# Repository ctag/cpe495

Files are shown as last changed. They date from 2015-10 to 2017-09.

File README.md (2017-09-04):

# cpe495

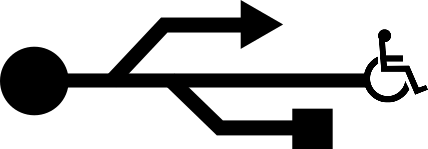
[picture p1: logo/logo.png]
Project Logo


UAH CPE495 "Adaptive H.I.D." senior design team.

## Current Development

Development on the 3.5mm adaptve button continues at https://github.com/ctag/clunke

## Git Formatting

* All paths and filenames should be camelCase.
* No binary files, they don't play well with git.
    * Images are an exception.

## Git Structure

* Git project for code, text documents.
* Github Wiki for research.
* Google Drive for presentations and binary files.

## What we're doing

Our team is researching and building Adaptive Technology interface devices to help people living with disabilities interact with computers.

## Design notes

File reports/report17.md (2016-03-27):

## Progress Report 17

Class | Week
----- | ----
CPE 496 | 9 Mar. 2016 -- 15 Mar. 2016

### Adaptive H.I.D.

<!--- This is a comment
Make sure to use *asterisks* to create italics on the member of whoever created the report
-->

* *Christopher Bero*
* Bryant Johnson
* John Gould
* Michael Baldwin

### Project Status
<!---
Project Status is a review of what was accomplished last week and a description of where we stand going into this sprint. A comparison between goals and actual accomplishments is a good idea.
-->

We are working to use the feedback provided at our last customer meeting to deliver another iteration of our prototype keyboard, along with an AT button to use with standardized 3.5mm cables found in many adaptive toys and machines.

### Difficulties Encountered

<!---
Difficulties Encountered is required. Other teams report losing points if this is missing.
Put here any trouble we had while accomplishing work during the previous sprint/week.
-->

Our 3D printer has developed a problem where the filament we have will swell slightly in some areas and bind inside of the hotend's mount. This causes us to lose the active print, as plastic stops extruding, and to recover we have to tear down the printer's extruder and remove the stuck filament.

### Next Sprint

<!---
Next Sprint should be a list of tasks that each member is going to work towards for the upcomming week.
Make sure to email members on Thursday or Friday so that they can respond with their most recent progress.
-->

* Christopher Bero:
    * Move 3d printer to makers local again
    * print button test base
* Michael Baldwin:
    * Continue work on predictive text application.
* John Gould:
    * Mediate testing and integration for hardware and software testing.
* Bryant Johnson:
    * Polyfill between hardware and software as support.

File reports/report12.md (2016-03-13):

## Progress Report 12

Class | Week
----- | ----
CPE 496 | 3 Feb. 2016 -- 9 Feb. 2016

### Adaptive H.I.D.

<!--- This is a comment
Make sure to use *asterisks* to create italics on the member of whoever created the report
-->

* *Christopher Bero*
* Bryant Johnson
* John Gould
* Michael Baldwin

### Project Status
<!---
Project Status is a review of what was accomplished last week and a description of where we stand going into this sprint. A comparison between goals and actual accomplishments is a good idea.
-->

We have finished development plans for our second keyboard prototype. It is currently being constructed.

Work on our desktop application is ongoing.

### Difficulties Encountered

<!---
Difficulties Encountered is required. Other teams report losing points if this is missing.
Put here any trouble we had while accomplishing work during the previous sprint/week.
-->

We upgraded from a 30W to 100W chemical laser bed and have had huge difficulties working with the control software. DXF if the preferred format for migrating an SVG model to the laser, but DXF files exported by Inkscape fail to be processed. We're working on an export format such as PLT or HPGL, but both crash a python script in Inkscape when invoked.

*Update Feb. 9*

We're closing in on a working method for designing and cutting files with the 100W laser bed. SVG files are exported as EPS, which is run through a script based on the `pstoedit` command line utility. This results in a useable DXF file which the laser computer recognizes. We're still investigating this approach, but it appears that color masks and layering works correctly.

### Next Sprint

<!---
Next Sprint should be a list of tasks that each member is going to work towards for the upcomming week.
Make sure to email members on Thursday or Friday so that they can respond with their most recent progress.
-->

* Christopher Bero:
    * Work on laser and keyboard hardware.
* Michael Baldwin:
    * Continue work on predictive text application.
* John Gould:
    * Mediate testing and integration for hardware and software testing.
* Bryant Johnson:
    * Polyfill between hardware and software as support.

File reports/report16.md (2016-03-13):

## Progress Report 16

Class | Week
----- | ----
CPE 496 | 2 Mar. 2016 -- 8 Mar. 2016

### Adaptive H.I.D.

<!--- This is a comment
Make sure to use *asterisks* to create italics on the member of whoever created the report
-->

* *Christopher Bero*
* Bryant Johnson
* John Gould
* Michael Baldwin

### Project Status
<!---
Project Status is a review of what was accomplished last week and a description of where we stand going into this sprint. A comparison between goals and actual accomplishments is a good idea.
-->

During this sprint we will meet with our customer again and go over the next keyboard prototype.
We went over various hardware design iterations. This sprint we tested the various methods of paddle actuation stiffness for the keyboard.

### Difficulties Encountered

<!---
Difficulties Encountered is required. Other teams report losing points if this is missing.
Put here any trouble we had while accomplishing work during the previous sprint/week.
-->

Different tension springs were causing problems. Need to purchase 3mm couplers for the keyboards layers.
Might need to buy spacers if not available. We were able to create a more streamlined solution for our laser cutter. Prototypes are being created at a much faster pace. 

### Next Sprint

<!---
Next Sprint should be a list of tasks that each member is going to work towards for the upcomming week.
Make sure to email members on Thursday or Friday so that they can respond with their most recent progress.
-->

* Christopher Bero:
    * Build second prototype keyboard.
* Michael Baldwin:
    * Continue work on predictive text application.
* John Gould:
    * Mediate testing and integration for hardware and software testing.
* Bryant Johnson:
    * Polyfill between hardware and software as support.

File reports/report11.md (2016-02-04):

## Progress Report 11

Class | Week
----- | ----
CPE 496 | 27 Jan. 2016 -- 2 Feb. 2016

### Adaptive H.I.D.

<!--- This is a comment
Make sure to use *asterisks* to create italics on the member of whoever created the report
-->

* Christopher Bero
* *Bryant Johnson*
* John Gould
* Michael Baldwin

### Project Status
<!---
Project Status is a review of what was accomplished last week and a description of where we stand going into this sprint. A comparison between goals and actual accomplishments is a good idea.
-->

We are working on our topical presentation, we will discuss the prospective future of consumer 3d printing with the class as well as the tests and findings we obtained through operation of our own printer.

Current goal is to design and upload a website detailing our project's goals and progress. 

We outlined our individual short term goals for this semester. 

### Difficulties Encountered

<!---
Difficulties Encountered is required. Other teams report losing points if this is missing.
Put here any trouble we had while accomplishing work during the previous sprint/week.
-->

Continual time conflicts create delays in our group meetings. Additionally, we have continued to encounter issues with scheduling within the course, as there does not seem to be a central calendar where class times and locations are posted.

### Next Sprint

<!---
Next Sprint should be a list of tasks that each member is going to work towards for the upcomming week.
Make sure to email members on Thursday or Friday so that they can respond with their most recent progress.
-->

* Christopher Bero:
    * Finalize second prototype keyboard made of laser cut acrylic. Begin gathering footage for the Team Video. 
* Michael Baldwin:
    * Begin construction of the website for the course. Continue work on predictive text application.
* John Gould:
    * Work on the Honors report. Mediate testing and integration for hardware and software testing.
* Bryant Johnson:
    * Update team bulletin board. Begin on construction of Team Poster. Contact TASC to schedule a design review meeting.

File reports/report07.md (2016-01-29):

## Progress Report 7

Class | Week
----- | ----
CPE 495 | 16 Nov. 2015 -- 20 Nov. 2015

### Adaptive H.I.D.

<!--- This is a comment
Make sure to use *asterisks* to create italics on the member of whoever created the report
-->

* *Christopher Bero*
* Bryant Johnson
* John Gould
* Michael Baldwin

### Project Status
<!---
Project Status is a review of what was accomplished last week and a description of where we stand going into this sprint. A comparison between goals and actual accomplishments is a good idea.
-->

We've completed another hardware purchase order for prototyping materials (PCB and breadboard) and 3.5mm mono audio equipment to match the standards discussed with our customer. 

We have an initial MSP-USB firmware demo and are working on the SPI tools to upload it to our experimenter board. 

We are still looking for project maintainers to contact for our software research.

### Difficulties Encountered

<!---
Difficulties Encountered is required. Other teams report losing points if this is missing.
Put here any trouble we had while accomplishing work during the previous sprint/week.
-->

The MSP430F5529 Experimenter Board has an on-PCB MSP430F2258 that's used for SPI and real time debugging. This chip is also the only way to flash new firmware to the F5529, making the upload process more complicated when using raw firmware rather than Energia sketches. We're pursuing a fix by flashing firmware with a modified version of avrdude.

### Next Sprint

<!---
Next Sprint should be a list of tasks that each member is going to work towards for the upcomming week.
Make sure to email members on Thursday or Friday so that they can respond with their most recent progress.
-->

* Christopher Bero:
    * Flash USB firmware demo to MSP430F5529.
    * Create 12-switch prototype circuit.
* Michael Baldwin:
    * Continuation of sprint 6.
* John Gould:
    * Continuation of sprint 6.
* Bryant Johnson:
    * Finalize interim report for CPE 495.

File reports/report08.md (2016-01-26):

## Progress Report 8

Class | Week
----- | ----
CPE 496 | 6 Jan. 2016 -- 13 Jan. 2016

### Adaptive H.I.D.

<!--- This is a comment
Make sure to use *asterisks* to create italics on the member of whoever created the report
-->

* *Christopher Bero*
* Bryant Johnson
* John Gould
* Michael Baldwin

### Project Status
<!---
Project Status is a review of what was accomplished last week and a description of where we stand going into this sprint. A comparison between goals and actual accomplishments is a good idea.
-->

We have gotten some firmware bugs ironed out during the winter break, the predictive application is undergoing some review of target platforms and database systems.

The team will break from work on the project to prepare a regurgitation of the previous semesters presentation that's been requested.

### Difficulties Encountered

<!---
Difficulties Encountered is required. Other teams report losing points if this is missing.
Put here any trouble we had while accomplishing work during the previous sprint/week.
-->

We are interested in doing most of the prototyping via chemical laser beds due to the speed and cost effective iteration, but some aspects of the prototype keyboard in our design result in weak joints and poor movement. We need to look into either kickstarting the 3d printing early or working with better resolution models on the laser.

### Next Sprint

<!---
Next Sprint should be a list of tasks that each member is going to work towards for the upcomming week.
Make sure to email members on Thursday or Friday so that they can respond with their most recent progress.
-->

* Christopher Bero:
    * Work on presentation regurgitation.
* Michael Baldwin:
    * Work on presentation regurgitation.
* John Gould:
    * Work on presentation regurgitation.
* Bryant Johnson:
    * Work on presentation regurgitation.

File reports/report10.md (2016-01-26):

## Progress Report 10

Class | Week
----- | ----
CPE 496 | 20 Jan. 2016 -- 26 Jan. 2016

### Adaptive H.I.D.

<!--- This is a comment
Make sure to use *asterisks* to create italics on the member of whoever created the report
-->

* *Christopher Bero*
* Bryant Johnson
* John Gould
* Michael Baldwin

### Project Status
<!---
Project Status is a review of what was accomplished last week and a description of where we stand going into this sprint. A comparison between goals and actual accomplishments is a good idea.
-->

We are working on our topical presentation, we will discuss the prospective future of consumer 3d printing with the class as well as the tests and findings we obtained through operation of our own printer.

The firmware is prepared for another keyboard prototype, which will have components laser cut on the 26th and 3d printed on the 27th. We need more mx switches for prototyping, a purchase order is being assembled, will likely be sent next week.

### Difficulties Encountered

<!---
Difficulties Encountered is required. Other teams report losing points if this is missing.
Put here any trouble we had while accomplishing work during the previous sprint/week.
-->

The firmware is proving to be incredibly difficult to write in such a manner that the keyboard operates as smoothly as an end user will expect. Making sure the states cascade properly as the buttons associated with characters is requiring a lot of developer testing.

### Next Sprint

<!---
Next Sprint should be a list of tasks that each member is going to work towards for the upcomming week.
Make sure to email members on Thursday or Friday so that they can respond with their most recent progress.
-->

* Christopher Bero:
    * Assemble second sliding keyboard prototype. Begin creating braille keyboard.
* Michael Baldwin:
    * Continue work on predictive text application.
* John Gould:
    * Mediate testing and integration for hardware and software testing.
* Bryant Johnson:
    * Polyfill between hardware and software as support.

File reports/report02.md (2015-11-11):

## Progress Report 2

Class | Week
----- | ----
CPE 495 | 12 Oct. 2015 - 16 Oct. 2015

### Adaptive H.I.D.

* Christopher Bero
* Bryant Johnson
* *John Gould*
* Michael Baldwin

### Project Status

- Attempted to contact organizations that are relevant to our product for testing and feedback (UCP NFB UAH DSS ADIB).
- We have gotten response from UCP and UAHDSS.
- Prepared purchasing guidelines for prototype materials.
- Gave project presentation to the class.
- Updated scope of projected, adjusted long term goals in case of difficulty.

### Difficulties Encountered

Firmly establishing contact has been slower than anticipated. The biggest criticism from the presentation was our lack of contact with potential customers. We have increased efforts of contact, with mixed results.

### Next Sprint

For the next reporting period we intend to:

-Begin investigation into the software aspect of the project.
-Order materials for construction of the prototype.
-Assess any changes to project details based on presentation.

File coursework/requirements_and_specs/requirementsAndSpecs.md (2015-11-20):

## Requirements Specification & Project Management Exercise 

Team 		| Class 	| Week
---- 		| ----- 	| ----
Adaptive H.I.D.	| CPE 495 	| 9 Nov. 2015 -- 14 Nov. 2015

### Problem Statement

Computers have dropped in price, grown in capability, and leapt into consumer markets in the past few years. Adaptive Technologies (AT) which help persons living with disability interface with a computer have been left behind in this regard. Solutions available are expensive and difficult to obtain. There is a distinct need for human interface devices which meet many AT requirements and are available to wider audiences for more reasonable cost.

### Project Objective Statement

Create and study affordable AT that can be crowdsourced and brought to people who currently can't access it.

### Marketing Requirements

* **Open Source Design**
    * Make design conducive to materials and tools available to makerspaces.
    * Put extra effort towards making the device easy to customize and iterate upon.
    * Use low cost machinery and materials.
* **Easy to Operate**
    * Must provide as good or better functionality than commercial equivalent.
    * Should be decently portable.
* **Reliable**
    * Must accept all possible input.
    * Must have a robust mechanical design.

### Objective Tree or Affinity Diagram

### Engineering Requirements

#### Sliding and Braille Keyboards

* **Hardware bounce time during activation:** <6ms
* **10 Million cycle lifetime.**
* **User Operation**
    * 30 Words per minute
    * 90% Typing accuracy
* **Materials**
    * Thermoplastics -- Case, Mounts
    * Stainless Steel -- Springs, Case
    * Gold Alloy -- Switch Contacts
* **PCB**
    * PCB should be at most 2-layer.
    * PCB should be dispersed enough in design to be easily fabricated with laserjet/home solutions.

#### Sliding Keyboard

* **Keymap**
    * Without layering: 36 possible characters.
        * Holds [A-Z] and special characters.
    * With layering: 180 possible characters.
        * Holds all of ASCII.

#### Braille Keyboard

* **Keymap**
    * 8 Keys for extended Braille.

### Constraints and Standards

#### Constraints

* **Target Price Point:** <$150
* **Portability**
	* Should be straightforward to move.
* **2-Layer PCB Designs**
    * More complicated implementations remove the prospect of home manufacturing.
* **Software**
    * Must work on low power ARM SoCs.

#### Standards

* **USB HID Profiling**
	* Must be recognized as an interface device.
	* USB standard 1.1 or 2.0.
* **3.5mm Mono Jack**
	* Used in a multitude of existing AT interface systems.

### Work Breakdown Structure

|       | Activity                                   | Description                                                                                                     | Deliverables/Checkpoints                                              | Duration (days)               | People | Resources | Predecessors |       |       | 
|-------|--------------------------------------------|-----------------------------------------------------------------------------------------------------------------|-----------------------------------------------------------------------|-------------------------------|--------|-----------|--------------|-------|-------| 
| 1     | Hardware Design                            |                                                                                                                 |                                                                       |                               |        |           |              |       |       | 
| 1.1   | Plan Switch Configuration                  | "Design a basic plan for the keyboard, specificially the placement of the switches."                        | Initial product design sketch | 7      | Chris     |              |       |       | 
| 1.2   | Design Circuitry                           | Design the circuit necessary in order implement the planned switch placement                                    | Circuit schematic                                                     | 1                             | Chris  |           | 1.1          |       |       | 
| 1.3   | Purchase Components                        |                                                                                                                 |                                                                       | 7                             | Chris  |           | 1.1          |       |       | 
| 1.4   | Construct Prototype                        | Build and test our prototype.                                                                                   |                                                                       |                               |        |           |              |       |       | 
| 1.4.1 | Construct a base                           | "Construct a platform which holds our microprocessor and switches, the switches are to be aligned based on our initial product sketch." |                               | 7      | "Chris, Trey"       |       | 1.3   | 
| 1.4.2 | Apply the Circuit                          | Connect the switches to the microprocessor through use of the schematic designed earlier.                       |                                                                       | 2                             | Trey   |           | 1.4.1        |       |       | 
| 1.4.3 | Provide a method of activating each switch | Add a device between the switches which allows each one to be activated.                                        |                                                                       | 5                             | "Chris, Trey"    |              | 1.4.1 |       | 
| 1.5   | Program Prototype                          |                                                                                                                 |                                                                       |                               |        |           |              |       |       | 
| 1.5.1 | Establish Input                            | Read input from each switch on the microcontroller                                                              | Test data                                                             | 1                             | "Trey, Bryant"  |              | 1.4.2 |       | 
| 1.5.2 | Interpret Input                            | Program the character representation for each input from the keyboard.                                          | Test data                                                             | 2                             | "Trey, Mike, Bryant"     |       | 1.5.1 | 
| 1.5.3 | Configure Output                           | Output the character last input from the keyboard to the client.                                                | Test data                                                             | 5                             | "Trey, Bryant"  |              |       |       | 
| 2     | Software Design                            |                                                                                                                 |                                                                       |                               |        |           |              |       |       | 
| 2.1   | Research Software                          | Research available opensource software for both text prediction and text to speach applications                 |                                                                       | 14                            | Mike   |           |              |       |       | 
| 2.2   | Software Planning                          |                                                                                                                 |                                                                       |                               |        |           |              |       |       | 
| 2.2.1 | Plan Text Prediction                       | Either plan a new text prediction program from scratch or plan how to reimpliment existing opensource software. | Flowchart and program description for text prediction                 |                               |        |           | 2.1          |       |       | 

### Schedule Gantt Chart

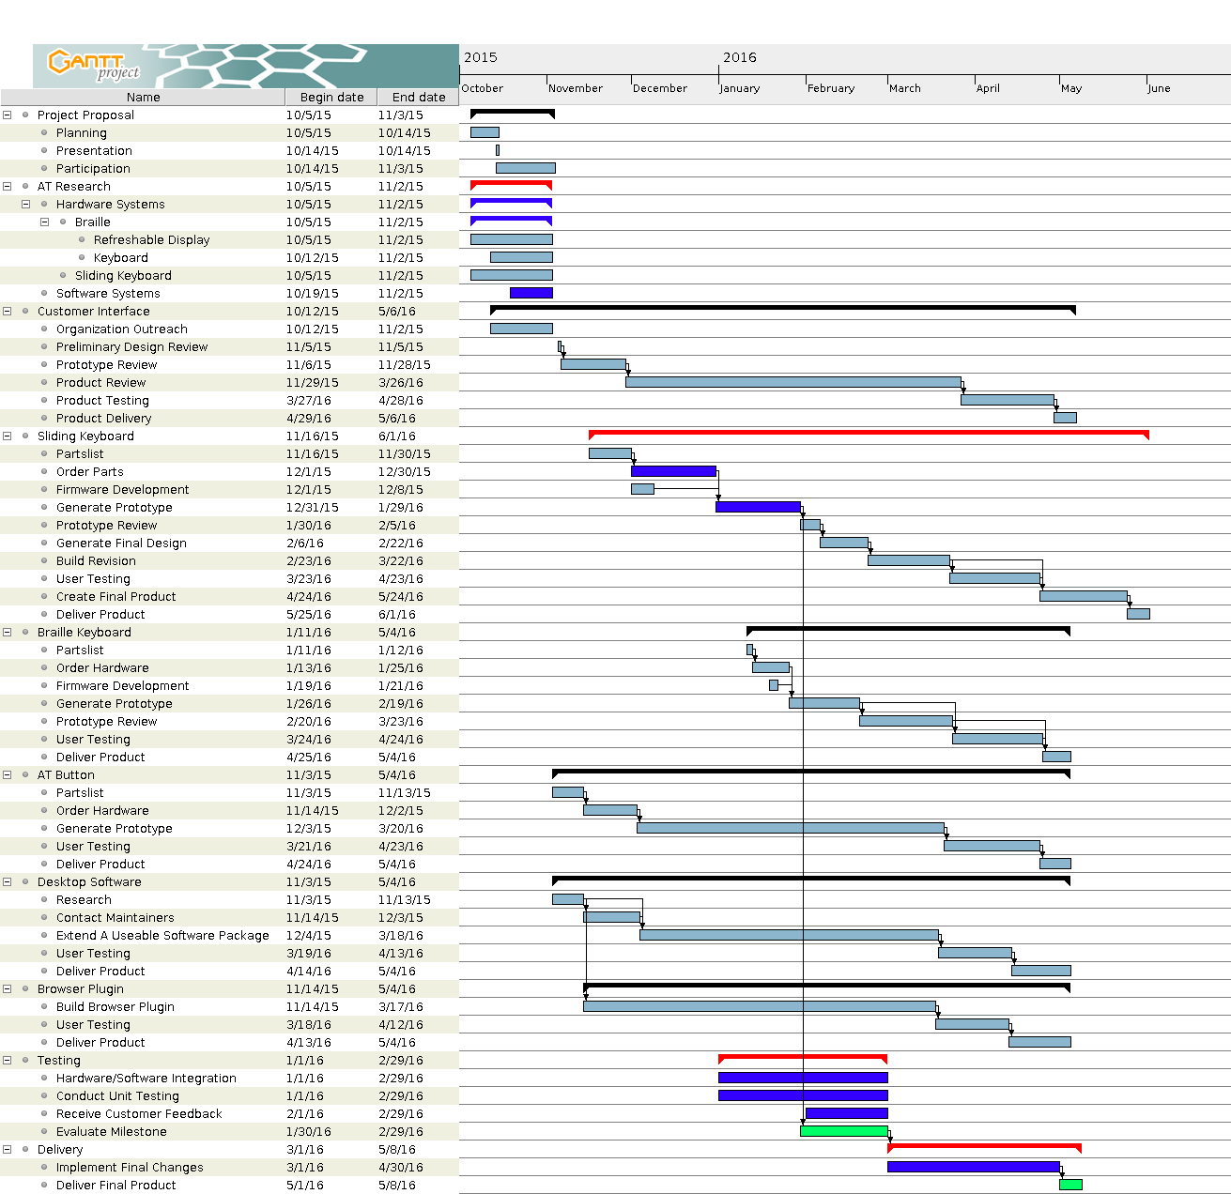
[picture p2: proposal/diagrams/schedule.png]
Team Workflow Gantt Chart Schedule


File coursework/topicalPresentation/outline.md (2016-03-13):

### Topical Presentation Outline
#### Adaptive H.I.D.

----

1. Review
	1. What are 3D printers
	2. A brief history
	3. The Reprap community

2. Challenges we face
	1. Material defects
	2. Mechanical defects
	3. Operator overhead

3. Investigation of serialization
	1. Why serialize
	2. Existing work
	3. Our approach

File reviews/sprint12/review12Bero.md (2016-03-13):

## Sprint 12 Hours - Christopher Bero

Class | Week
----- | ----
CPE 496 | 3 Feb. 2016 -- 9 Feb. 2016

### Sprint Stories

* Collect acrylic sheets for laser cutting
* 3D print switch mounts
* Laser cut keyboard backplane
* Create and send topical presentation overview

### Task Notes

#### 3 Feb. 2016

* Documentation
	* 1 hour

#### 4 Feb. 2016

* keyswitch mounting CAD
	* 2 hours

#### 5 Feb. 2016

* Laser Cutting Safety Class
	 * 2 hours
* Laser Cutting
	* 2 hours

#### 6 Feb. 2016

* 3D Printing
	* 6 hours

#### 7 Feb. 2016

* 3D Printing
	* 2 hours

#### 8 Feb. 2016

* Troubleshooting 100W laser
	* 7 hours
* Class
	* 1.5 hours

#### 9 Feb. 2016

* Team Meeting
	* 1 hour
* Laser cutting and demo assembly
	* 5 hours

#### Hours total: 29.5

<br><br><br><br><br><br>
<br><br><br><br><br><br>

---

Signed:

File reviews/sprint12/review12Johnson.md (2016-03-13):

## Sprint 12 Hours - Bryant Johnson

Class | Week
----- | ----
CPE 496 | 3 Feb. 2016 -- 9 Feb. 2016

### Sprint Stories

* Contacted TASC and set up meeting times.
* Updated Team Bulletin Board
* Begin Team Poster
* Assist with keyboard hardware design.

### Task Notes

#### 3 Feb. 2016

* Documentation Updates - Sprint Reviews
	* 1 hour
* Set up meeting with TASC
	* 2 hour

#### 4 Feb. 2016

* Bulletin Board Update
	* 1 hour

#### 6 Feb. 2016

* Begin Team Poster Construction
	* 1 hour
* Documentation Update - Purchases
	* 1 hour

#### 9 Feb. 2016

* Team Meeting
	* 1 hour
* Laser cutting and demo assembly
	* 5 hours
	
#### Hours total: 12

<br><br><br><br><br><br>
<br><br><br><br><br><br>

---

Signed:

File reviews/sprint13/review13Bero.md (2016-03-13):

## Sprint 13 Hours - Christopher Bero

Class | Week
----- | ----
CPE 496 | 10 Feb. 2016 -- 16 Feb. 2016

### Sprint Stories

* Finish and deliver topical presentation
* Finish and present keyboard prototype

### Task Notes

#### 10 Feb. 2016

* Working on topical presentation
	* 1 hour

#### 11 Feb. 2016

* Finalizing topical presentation document
	* 2 hours
* Class and topical presentation
	* 1 hour
* Laser cutting demo for TASC meeting
	* 7 hours (12-1am from the next day here)

#### 12 Feb. 2016

* TASC Meeting
	* 2 hours

#### Hours total: 12

<br><br><br><br><br><br>
<br><br><br><br><br><br>

---

Signed:

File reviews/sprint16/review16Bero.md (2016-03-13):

## Sprint 16 Hours - Christopher Bero

Class | Week
----- | ----
CPE 496 | 2 Mar. 2016 -- 8 Mar. 2016

### Sprint Stories

* Work on improved code base for msp430
* finish next keyboard

### Task Notes

#### 2 Mar. 2016

* Working at makerslocal
	* paperwork backlog
	* laser files
	* keyboard handle mount
	* 3d printing repair
	* hours: 8

#### 3 Mar. 2016

* Working at makerslocal (and into 4am 4th of March)
	* Laser cutting
	* Prototype keyboard 2 assembly
	* hours: 10

#### 4 Mar. 2016

* TASC Meeting
	* Got feed back
	* Next meeting 14 March
	* hours: 3

#### 5-6 Mar. 2016

* Team work-meeting
	* Working on next keyboard design
	* hours: 8

#### 8 Mar. 2016

* Working on firmware and button
	* hours: 4

#### Hours total: 33

<br><br><br><br><br><br>
<br><br><br><br><br><br>

---

Signed:

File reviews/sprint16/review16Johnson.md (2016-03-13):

## Sprint 16 Hours - Bryant Johnson

Class | Week
----- | ----
CPE 496 | 2 Mar. 2016 -- 8 Mar. 2016

### Sprint Stories

* Finish next keyboard prototype. This sprint we spent many hours creating and revising the hardware prototype layouts. We had to purchase more material in search of alternatives for the paddle.

### Task Notes

#### 2 Mar. 2016

* Working at makerslocal. Designed new prototype layouts. 
	* 5 hours

#### 3 Mar. 2016

* Created new prototype. Tested multiple iterations. Wired up the new design and began working on the firmware. 
	* 12 hours
	
#### 4 Mar. 2016

* Documentation Updates - Sprint Reviews
	* 1 hour
* Meeting with TASC. Discuss the hardware design and planned final revisions.  
	* 2 hours
	
#### Hours total:

<br><br><br><br><br><br>
<br><br><br><br><br><br>

---

Signed:

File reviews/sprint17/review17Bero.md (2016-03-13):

## Sprint 16 Hours - Christopher Bero

Class | Week
----- | ----
CPE 496 | 9 Mar. 2016 -- 15 Mar. 2016

### Sprint Stories

* Work on improved code base for msp430
* finish next keyboard

### Task Notes

#### 10 Mar. 2016

* Working at makerslocal
	* Hours 6

#### 11 Mar. 2016

* Working on firmware
	* Hours 3

#### 13 Mar. 2016

* Laser cut next keyboard and 3d print button
	* Hours 8

#### Hours total:

<br><br><br><br><br><br>
<br><br><br><br><br><br>

---

Signed:

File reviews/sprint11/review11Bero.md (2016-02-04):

## Sprint 11 Hours - Christopher Bero

Class | Week
----- | ----
CPE 496 | 27 Jan. 2016 -- 2 Feb. 2016

### Sprint Stories

* Collect acrylic sheets for laser cutting
* Purchase additional switches
* 3D print switch mounts
* Laser cut keyboard backplane
* Create and send topical presentation overview

### Task Notes

#### 28 Jan. 2016

* Class
    * 1.5 hours
* Documentation
	* 1 hour
* Developing SCAD code for printed mounts
    * 3 hours

#### 29 Jan. 2016

* Printing test pieces
	* 1 hour

#### 1 Feb. 2016

* Researching Acrylic vendors
	* 3 hours

#### 2 Feb. 2016

* Test fitting switch mounts
	* 1 hour
* Purchased 50 more mx switches
	* 2 hours
* Class
	* 1.5 hours

#### Hours total: 14

<br><br><br><br><br><br>
<br><br><br><br><br><br>

---

Signed:

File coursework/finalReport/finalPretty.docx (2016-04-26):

Adaptive H.I.D.


https://github.com/ctag/cpe495

http://cpe-design.uah.edu/2016/team1/index.html


CPE 496 Final Report

Spring 2016

University of alabama in huntsville

301 Sparkman Dr. NW, Huntsville, Alabama 35899

Christopher Bero

Bryant Johnson

Michael Baldwin
John Gould

# Project Summary

Design a set of adaptive interface devices for modern computers with readily available consumer machinery and products. The product will have a focus on affordability, iterative design, and easy operation. Construct and test the devices for viability in general use; then generate a case study on the effectiveness of this approach to bringing adaptive technology to a larger audience.

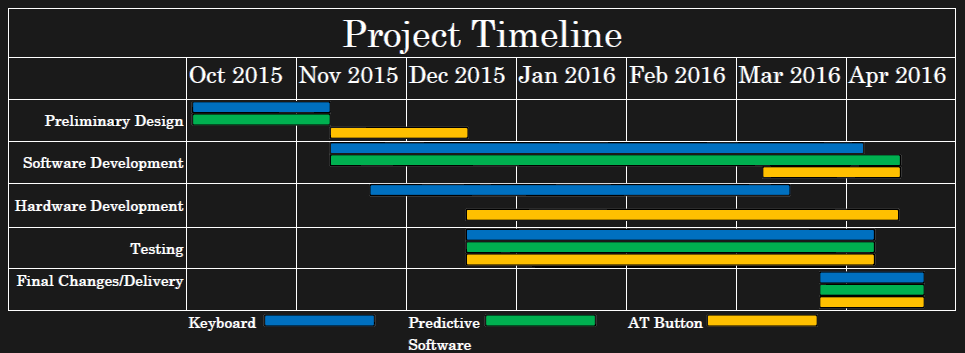
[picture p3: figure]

# Team Description

The Adaptive H.I.D. project was envisioned to develop affordable computer interface devices and bring adaptive technology to more people around the world. Each team member was selected based on how their personal expertise would benefit the project.

Chris Bero is the Hardware Lead for the project with the subtask of community outreach. He originally conceptualized the project after noticing the many shortfalls of adaptive technology in his free time and drafted multiple designs that could benefit the disabled community. He is very knowledgeable in microcontrollers, 3D printers, and collaborative software development.

Michael Baldwin is the Software Lead for the project. He leads the pursuit in either upgrading an existing package or creating our own custom keyboard interface which uses predictive text to lessen the number of characters required to complete a word. Michael has a very strong programming background and implements professional modern style when developing code.

Bryant Johnson is the Testing Lead with the subtask of technical writer. He is responsible for creating the unit tests and maintaining the documentation of the entire project. He excels in strategizing the project and rationalizing each process while paying attention to fine details. His interest includes cybersecurity and reverse engineering.

John Gould is the Systems Lead for this project. He is responsible for integration of the hardware and software that will be developed for this project and will ensure that the mechanical elements will work together in the finished product. His strengths include microcontroller based projects and software development.

# Design Problem

Our team is researching and building Adaptive Technology human interface devices to help people living with disabilities interact with computers. Adaptive technology (AT) is a device or component which is specifically designed for persons with disabilities. Human Interface Devices (H.I.D) is a method by which a human interacts with an electronic information system either by input or output. Computers have dropped in price, grown in capability, and leapt into consumer markets in the past few years. Adaptive Technologies which help persons living with disability interface with a computer have been left behind in this regard. Solutions available are expensive and difficult to obtain. There is a distinct need for human interface devices which meet many AT requirements and are available to wider audiences for more reasonable cost. This project is going to be a student lead and noncommercial in nature. We wish to make clear that our design decision to present the project as open source incurs additional work for us to have a clean operating environment that others can approach and utilize in separate projects, not a sidestepping of features we do not intend to implement. We are developing two interfaces that include a Sliding Keyboard, and a AT Button. The sliding keyboard will require no finger movement to type characters, instead utilizing shoulder and elbow ranges. Our AT Button was created as a result from our customer requesting us to investigate the idea. We are interfacing with local disability service groups United Cerebral Palsy (UCP) of Huntsville Technology Assistance for Special Consumers (TASC)

We established our marketing and engineering requirements based upon UNICEF’s World Report on Disability. UNICEF states, “Manufacturing or assembling [AT] products locally, using local materials, can reduce cost and ensure that devices are suitable for the context.” Priority of the design was for cheap and readily available materials and techniques—allowing for the product to be easy to build and modify. Consumers should be able to with relative ease assemble the device themselves. Additionally, we wanted to build a product with equivalent or better functionality without increasing complexity of user interaction. The design should be durable and adhere to the standards of current AT marketable solutions. The Marketing Requirements are as follows:

- Open Source Design
  - Require only items available to common makerspaces
  - Easy to iterate and customize
  - Low cost requirements for parts and machinery
- Easy to Operate
  - Must provide as good or better functionality than existing solutions
- Reliable
  - Must accept improper input and have a robust mechanical design.

The Engineering Requirements were based upon current mechanical keyboard design standards. We needed the hardware to react to changes under 6 milliseconds while in use. Each switch will need to last at least 10 Million cycles while supporting at least 30 words per minute operation at 90% accuracy. The device should be operational from -10 Degrees Celsius up to 70 Degrees Celsius. These requirements are typically found on the product speciation section of modern mechanical keyboards by various brands on the marketplace. Research was conducted by browsing and comparing specifications of listed items in retail stores.

# Background Information

There are many shortfalls when it comes to AT. The main issue is that there is high development costs to a low volume market. Existing products include a Large Switch Keyboard which is aimed towards people with motor disabilities and lack of precision. It is less costly but does not necessarily solve the problem just lessens the possibility of error. The Orbitouch by Blue Orb Inc. is the main system that we based our design from. The keyboard retails for $450 with eight sections for character selection and the ability to simulate a mouse.

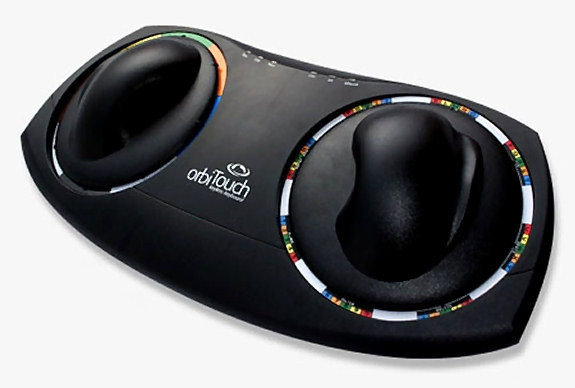
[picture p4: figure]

Figure 1 Http://orbitouch.org/

In lieu of any legal advice available to us, we read all of Blue Orb Inc’s listed patents based on the design. Our research found that the patents covered the mechanical design of the internal mechanisms of the keyboard. We moved our design approach to have our AT keyboard use the key map of Orbitouch.

Our team began to pursue creating the AT Button after our first keyboard design review with UCP TASC. TASC specifically asked us to investigate the creation of AT Buttons because of their current costs and need. Currently, AT Buttons are sold in the range of $60 - $160 and are out of the budget of many families coping with disabilities.

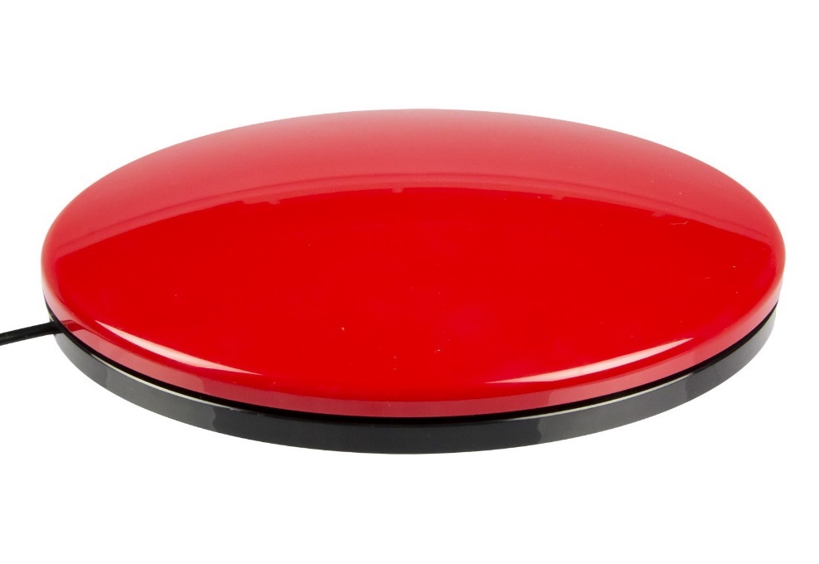
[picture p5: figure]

Figure 2 http://www.boundlessat.com/Switches/Wired-Switches/Big-Buddy-Buttons

We wanted to create a solution that was able to be made easily by home consumers by using a 3D printer.

The most significant differences between competing products versus our product is the low price and iterative design. We strive to create and publish an open source product that will allow people develop custom, low cost AT wherever a makerspace is available.

# Trade-off Analysis of Design Alternatives

Various alternative products were considered in the design of this project. We have reviewed the possibility of creating four different systems to be part of our suite of low cost AT devices that we will deliver as the outcome of our project. With our trade-off analysis we investigate the options available for our project and the design decisions which lead to our chosen systems.

## Products

Within the project of creating AT HID, our team generates several product ideas and needs to decide which are worth pursuing and how to go about designing the results.

Sliding keyboard. Our first product is a keyboard to limit the required dexterity of typing. Targeted at users with conditions commonly associated with amyotrophic lateral sclerosis or cerebral palsy, this keyboard removes keys from the user’s path and instead places two horizontal “pucks” down as control surfaces. Pucks can be a custom design from a handle to a joystick, anything that the user can operate to slide the base of the puck around an inset octagon that it resides on. At each corner of the octagon are mechanical switches, totaling sixteen between the two pucks. If each puck is moved to contact a switch, the full range of the QWERTY keyboard layout can be represented.

AT Button. While our customer expressed general interest in the above solutions, we also learned a lot about the current state of AT in use at UCP and received enough direction to build out our case study plan for more AT. One of the more common systems for actuation in use at UCP are SPST buttons -- roughly four-inch diameter pads -- that terminate to a 3.5mm mono audio pole. These buttons are then plugged into a variety of host items in order to provide a greater ease of access to the item. At UCP a conflict has occurred where the market price for these buttons is high -- in the $60 to $80 range -- and their use level is low -- an example is sub $20 toy adapting. We suspect this is caused by the quality of the buttons, if the button is associated with a device to request food or water, then it must work each and every time. Toy adapting isn’t quite as mission critical though, and a solution which provides “button to 3.5mm jack” at a lower price would be ideal. Thus we intend to investigate using mechanical keyboard switches with thermoplastic or acrylic cases to create more affordable actuation devices and test them as part of our case study.

Switch Circuits. For switches, we will use port inputs on either the MSP430 or ATmega and arrange switches with pulldown resistors.

Our plan is to implement a scanning grid for the switches as used in CPE322 for FPGAs.

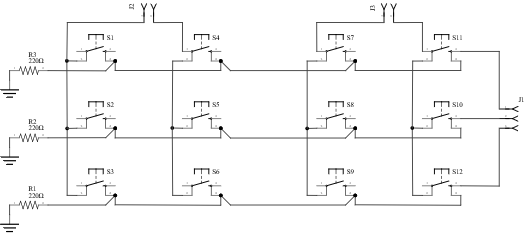
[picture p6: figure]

For testing our firmware and hardware approach, we constructed a set of twelve isolated switches which can be wired into breadboards. The tradeoff here is ease of configuration in exchange for a lot of tidiness.

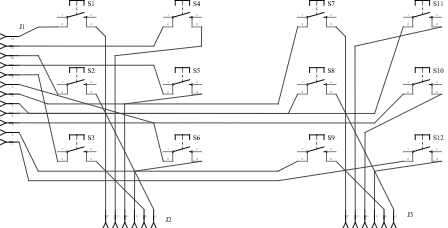
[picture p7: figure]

## Material breakdown for sliding keyboards

We’re following Design Analysis from the University of Delaware’s Nonprofit Management Certificate Course (http://www.udel.edu/ccrs/NPMCC_2006_Materials/Tradeoff_Analysis_Example.pdf).

For our design decisions, we hold the sliding keyboard to have similar enough hardware qualities as to occupy the same space of design approaches. Hardware approaches were based on components that we have had previous experience with, could easily source, and knew to have high availability in common makerspaces (PLA printing, 30W laser CNC bed).

Design Scenario A

- MSP430F5529 processor
- Cherry Corp. MX switches
- Thermoplastic case

Design Scenario B

- MSP430F5529 processor
- Gatereon switches
- Laser cut case

Design Scenario C

- ATmega328p processor
- Cherry Corp. MX switches
- Thermoplastic case

Design Scenario D

- ATmega328p processor
- Gatereon switches
- Laser cut case

Each approach’s set of decision criteria is given an importance magnitude 1-5 and instance rating 1-5. The resulting grade (= importance * rating) is assigned and reviewed alongside functional or behavioral decompositions.

Scenario A - Decision Criteria | Importance | Rating | Grade
Production Cost | 5 | 3 | 15
Component Availability | 4 | 2 | 8
Assembly Skill/Time | 4 | 3 | 12
System Durability | 3 | 4 | 12
Design Complexity | 2 | 3 | 6
Grade total | | | 53

Scenario B - Decision Criteria | Importance | Rating | Grade
Production Cost | 5 | 5 | 25
Component Availability | 4 | 4 | 16
Assembly Skill/Time | 4 | 4 | 16
System Durability | 3 | 2 | 6
Design Complexity | 2 | 4 | 8
Grade total | | | 71

Scenario C - Decision Criteria | Importance | Rating | Grade
Production Cost | 5 | 2 | 10
Component Availability | 4 | 3 | 12
Assembly Skill/Time | 4 | 4 | 16
System Durability | 3 | 4 | 12
Design Complexity | 2 | 4 | 8
Grade total | | | 58

Scenario D - Decision Criteria | Importance | Rating | Grade
Production Cost | 5 | 4 | 20
Component Availability | 4 | 5 | 20
Assembly Skill/Time | 4 | 5 | 20
System Durability | 3 | 2 | 6
Design Complexity | 2 | 4 | 8
Grade total | | | 74

Analysis factors

- Cherry Corp. products are often difficult to source, are more expensive than Gatereon compliments.
- Grading thermoplastic and laser laminate cases is difficult due to the vast plethora of available systems and operator knowledge. We settled on as unbiased a format as possible, with plastic cases offering better system durability and longevity with a higher complexity and design cost.
- The two microcontrollers compared here were chosen either for their popularity in crowd-designed keyboards (such as the Kiibohd Infinity) or their use in previous UAH courses (CPE323).
- We tried to favor availability and assembly factors heavily in this stage, as a durable and cheap system is unhelpful if nobody is willing or capable to generate them for people in need.

Although the Atmel/Gatereon solution provided the best score by our criteria, our team did not have a “will fetch a good grade” section. This unfortunately ended up being the deciding factor, and we chose to investigate the msp430/cherry/thermoplastic option as it used microcontrollers presented in a previous UAH class and promised a higher level of complexity. We wonder how often this happens in the real world.

# Design information & Test Scenarios

## Keyboard - Base materials

The team wanted to ensure that the keyboard provided a proper balance between being comprised of easy to source materials, designed to be easily assembled, and still highly function to the end user. We chose sheet-based materials in order to provide a wider array of assembly options. A 3-5mm thick sheet of material can be laser cut, routed on a CNC mill, or manually machined with a drill press, jigsaw, bandsaw, or coping saw. 3D printed components were utilized in such a way that they could be replaced by additional segments of sheet material glued into a 14mm square mount.

We tried a small grouping of woods and plywoods with our preferred method of prototyping: laser cut panels. Sanded plywood (3mm) available at local home improvement stores provided excellent results, especially when sealed with clear waterproofing. Warping did prove to have some detrimental effects, such that we suggest inspecting sheets before purchase, and then storing them in a cool, humidity controlled location. For a more industrial end product, we additionally chose 3-5mm acrylic sheets. We suspect these acrylic sheets entail more difficulty for CNC and hand crafted approaches, but they produce fantastic results on a laser cutter. While being subjected to the laser, acrylic will sublimate into a toxic [1] fume, which necessitated proper ventilation and operator procedures. During our use of the laser cutter, a two-stage external fan and vent system was kept running, and completed cuts were allowed to vent for several seconds before the laser enclosure was opened.

Other materials, such as the PVC pipe cap and springs, were selected as a “basic approach” in which we challenged ourselves to find local material sources. These materials served functional purposes well, though we support the notion that more tuned and ergonomic solutions exist. We believe that these improvements, such as 3D printed paddles, can be adjusted and implemented in the assembly process with minimal deviation from the overall design. The 4 inch PVC pipe caps are durable and can be easily machined and then used as sliders on both plywood and acrylic. Also, the PVC cap diameter falls close to the target maximum 3D printing footprint, so printing custom and ergonomic paddles is supported without modification to the keyboard’s structure.

One exception made was for an online order of M3 bolts. The keyboard can, with relative ease, be adjusted to use lasercut clips for joining the panels, but we desired more rigidity in the construction, as well as the ability to tear down the keyboard quickly without fear of breaking the pins.

## Keyboard - Microcontroller Hardware

We began the class by taking a look at microcontroller based USB clients. On either brand’s side we found solutions for emulating USB protocols in firmware or hardware level systems provided by the manufacturer. ATmel provides USB testing boards based on the AT90USB1287, which has full speed USB one-the-go (OTG) support [2]. Originally, the team intended to fabricate a custom PCB to mount either an MSP430F5529 LQFP IC or ATmega328P DIP package. After looking into online PCB manufacturing, we decided that the involved complexity, wait time, and cost were great enough that just mounting the default experimenter hardware into the keyboard produced more favorable results. To this end, the keyboard baseplate includes mounting points for a Ti MSP430F5529 Launchpad PCB. We wanted to investigate using V-USB [3] with an ATmega328 based Arduino, but eschewed it due to time constraints.

## Keyboard - Microcontroller Firmware

The discussion about which microcontroller package to use was occasionally a heated one. ATmel chips are easily the most well-known and implemented controllers for hobby level projects all over the world. But we had just spent a semester learning about the MSP430 architecture in CPE323, and wanted to implement something from it. The decision eventually came down to the results obtained from the section on microcontroller hardware, where the firmware level implementation on AVR, and hardware level versions of the MSP430 were the best candidates. Hardware USB support on the MSP430F5529 Experimenter Board was more favorable -- and we hoped more robust as well -- for delivery to an end-user than a firmware approach with ATmegas.

We were shocked by the loss of familiarity in developing MSP430 firmware. Texas Instruments now pushes a package called ‘driverlib’ heavily, in what appears to be an attempt to compete with the popularity of Arduino’s IDE. What results is less of a departure from formal C than the Processing-like code available in Arduino’s IDE, but it’s even more estranged and has a huge lack of clean programming interface left behind. In CPE323 I (writing as Chris Bero) enjoyed working with the control registeres and bitmasks. With Ti’s driverlib, that has all been replaced by a highly opaque suite of functions, which all have horrendously distended naming schemes such as:

GPIO_setAsInputPinWithPullDownResistor(LEFT_BUTTONS_PORT, LEFT_BUTTONS_PINS, GPIO_LOW_TO_HIGH_TRANSITION)

To properly interact with the hardware level USB support on the MSP430F5529, driverlib is required. This had us double-guessing the design decision, and by the end of the CPE496 semester, we had constructed a test-circuit for implementing HID USB from the V-USB package with an ATmega328 [4].

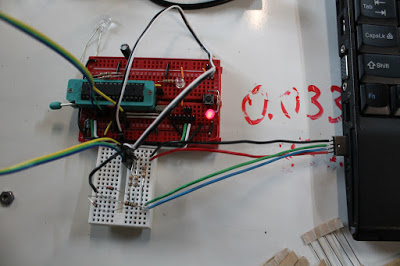
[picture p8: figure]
edit

Figure 3 Working ATmel USB support

## 3D Printer - Base System

As a prospective freshman, I (Chris Bero) was walked through the highbay machine shop in Tech Hall. During the tour, we were told that as engineering students we would have access to this facility and others like it around campus. Previously I had rejected internship offers at UAH, because I didn’t know if I could commit to enrolling. After that day touring campus I decided to become a student here. By the time I found myself signing up for CPE495 I had interacted with the machine shop manager several times, and fully understood that it was off limits except for a single semester if I took the appropriate machining class. Even then only projects for that class were allowed. Hurt feelings and mistrust aside, we entered CPE495 with the knowledge that we’d have to source the manufacturing equipment ourselves.

The team chose a Printrbot Simple Metal due to its price point, mechanical construction, and the background of Printrbot as a company that works with open source projects and contributes to the RepRap community [6]. We purchased the printer and assembled it at Makers Local 256, where we had access to staging space for printing close to campus.

## 3D Printer - Modifications

We quickly set about adjusting and building on the printer to create a machine capable of handling the proposed manufacturing and prototyping. The printer was paired with a Raspberry Pi which ran a website and camera for remote operation, along with an ATmega328 to control various elements such as lighting, fans, environment sensors, and heated build plates. We drafted our own filament guide design [7] and later pivoted to a PVC scaffolding which held filament reels above the printer to provide less chance of the filament breaking. The PVC later served as a structure to hold LED lighting and an area fan for the printer as well. While performing build plate material tests, we added a heated platform to the build plate, which was controlled in gcode.

The hotend was exchanged for a j-head MK-V [8]. The j-head is almost an entire inch shorter than the default Ubis hotend, and required modifications to the printer to be compatible. We initially tried printing an adapter socket which would mount in the extruder and then hold the j-head as low as the Ubis, but this broke twice while printing. We abandoned the adapter in favor of modifying the build plate, which was lifted on springs to meet the shorter hotend.

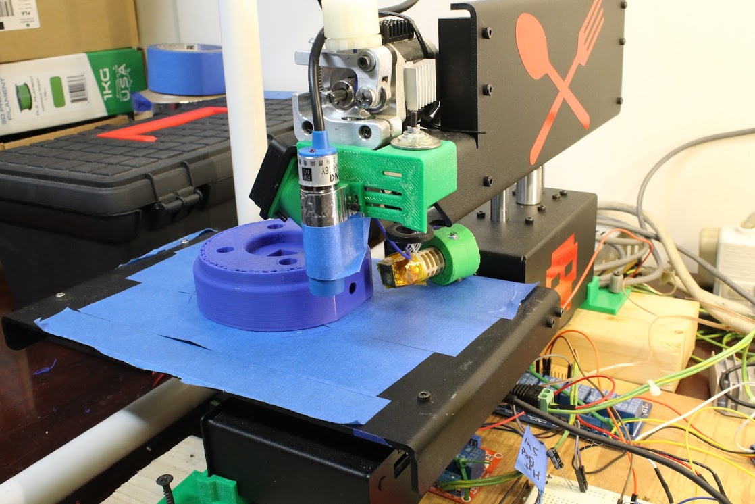
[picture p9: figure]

Figure 4 Replacement Inductive Sensor

During build plate material testing, we encountered a problem where the inductive Z-probe could not “see” the aluminum plate with our borosilicate glass plate mounted above it. To address this we purchased a more powerful inductive probe and designed an external harness to mount it on the extruder assembly.

The fan which came with the Simple Metal kit wore out partway through the CPE496 semester, and we replaced it with a more powerful blower fan, incidentally improving the quality of surface finishes on printed parts.

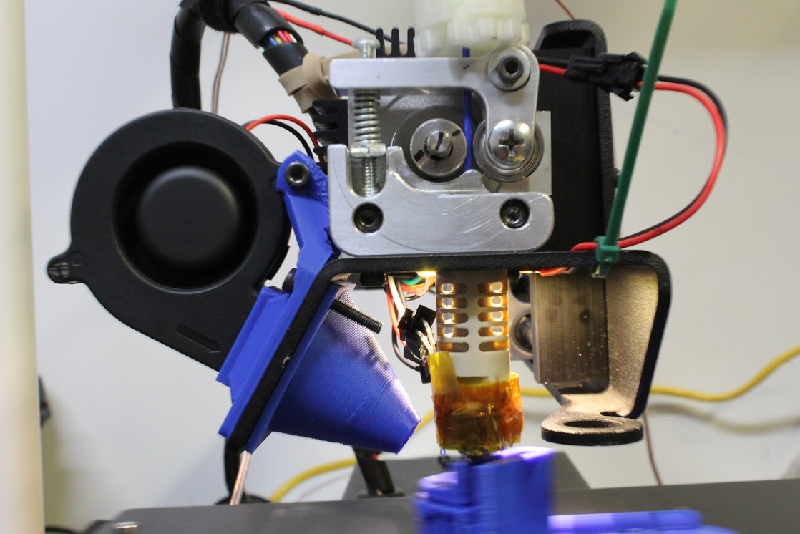
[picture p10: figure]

Figure 5 Blower fan addition

## 3D Printer - Build Plate Materials

We tested an assortment of materials based on discussions and posts available from RepRap’s wiki and forums.

### Aluminum

We tried printing directly to an aluminum plate. No plastic adhesion for either cool or heated build plate.

### Painters Tape

“Blue Tape” worked quite well on a cool print surface, but would not stick to heated aluminum. Parts adhered very well to the tape, but the stress of curling would usually break the tape from the build plate, causing a warped print and more time for cleanup and re-application of the tape.

### Kapton Tape

We had varied results with kapton tape. For the most part our results were similar to that of the plain aluminum, with the first layer of a part not adhering. Additionally, applying kapton tape to the build plate was by far the most intensive effort, as special care had to be given to avoid air bubbles trapped underneath.

### Polyetherimide (PEI) with 3M 468MP

PEI also delivered mixed results. We had some fantastic prints, where the part would adhere to a heated build plate with this material, and then almost pop free on its own after cooling. Unfortunately we couldn’t tie down consistent prints and had to move on.

### Polyetherimide/Fiberglass Laminate

We purchased this in the form of “Buildtak”, a commercial product. This material was very tricky to properly tune, with the initial layer of a part printed at precisely 0.2mm at 210 degrees C and 150% over extrusion. Once set up though, the Buildtak began delivering excellent results with minimal overhead. At one point we had a prototype AT button stick to the print plate so well that it could only be removed by cutting the Buildtak free. We chose this material as our best option.

### Borosilicate Glass

We tried many, many different forms of this approach. Glass with blue tape, glass with PEI, glass with Polyvinylpyrrolidone (PVP) glue painted onto it, glass with PVA glue painted onto it, glass with sandpaper glued to it, glass with kapton tape, and plain glass. Some worked better than others, and a few of these we would consider re-investigating with a manually leveled print bed (no inductive sensor). Ultimately none delivered consistent results.

## 3D Printer - Serialization

During the course of this class, we investigated the design of a serialized 3D printer. Current home-use printers require fairly involved human interaction for upkeep and operation overhead. In order to maximize the utility of our printer we wished for it to print consecutively both day and night. Conservative estimations would put the printer at 3 printed items per day as opposed to the 1 printed part per day we achieved with full operator involvement.

Our first approach was to design a custom Aluminum build plate which would include an actuated lever to detach finished parts. This design worked well initially, but a design flaw where the heated aluminum would warp due to the channel of missing material caused us to abandon it.

Next we constructed a print enclosure by which printed parts would be removed through the application of thermal expansion. We settled on Borosilicate glass as a fair candidate due to the glass’s tendency to stretch when heated. The heated build plate was modified to run over-spec at 480 Watts, and we affixed the glass above it. The process worked correctly: after printing a part, the heater would be cycled on and off several times over the course of two hours, which repeated stretching and contracting of the glass build material would cause printed parts to delaminate from it and they could then be easily knocked to the side, and another print could start. Unfortunately, we discovered toward the end of our investigation that unfavorable results (inconsistency of the first layers to a print) was likely due to a slight convex warp to the glass plate, where it curved 0.3mm from the edges to the center, which ruined the calibration of prints requiring a first layer of 0.2mm.

In conclusion to our serialization exercise, we find it to be a feasible end-goal at relatively low cost and simple assembly.

## AT Button - Design Aspects

We began working on the AT Button late in the class, and tried to account for the lack of time by designing to a useable first prototype. Our basis for form factor came from looking at images of available products and guessing at their size and structure. We then paired that with the information that the typical small print envelope size for a reprap is 120mm, and settled on a 100mm diameter button base. This was stretching the limits of our printing capabilities, so we paired additional work on the design of the part’s first few layers against the previous investigation into print plate materials.

## Predictive Text Application

The application takes input from the user using a textbox with a listener attached. This serves the purpose of listening for keystrokes. When a key is pressed, the application looks for the text the user is currently typing and presumes it is a partially completed word. The program then takes this word and asks a SQLite database for the 5 most likely completions to this word. The selected candidates are chosen based on frequency from the user, as well as alphabetical proximity to the letters already input so far.

The program consists of two primary objects: the listener is in the main object, while sql queries are handled by another object. This object is run on a child thread, allowing the user to continue using the application even while the sql object is waiting for a reply from the database. Within the main object, once the word to be completed is obtained, it is forwarded to the sql object and waits for it to reply with the five results. Once the potential candidates are calculated, each answer is posted to a button for the user to choose from. The sql object receives the partially completed word and stores it in a variable 'arg' and runs the following query: "SELECT WORD FROM dictionary WHERE WORD LIKE '" + arg + "%' ORDER BY COUNT DESC LIMIT 5;". The result is then parsed into an array of 5 strings and is sent to the main object.

The database consists of two columns: WORD and COUNT. The WORD column contains each word that can be recommended to the user, while the COUNT column determines which word is used more often than another. More specifically COUNT contains how many times that word has been chosen as the intended word and the word with the highest COUNT is considered to be the most likely to be used. Using this algorithm, the application will begin to learn what words really are more common for each user and will become more and more useful. The database is populated with the English dictionary and COUNT is initiated using various online articles so even on initial launch the application has a general idea of what words a random sampling of users prefers as their most used words.

# Cost Data

## October 2015

Item | Quantity | Sum Cost
Ti USB Developer Board | 2 | $38.90
ATmega328 | 4 | $6.99
Screw Terminal Blocks | 1 | $5.95
PCB proto board | 1 | $7.99
PCB proto board | 1 | $3.57
Breadboard | 1 | $3.58
Cherry Mx switches | 24 | $26.74

Subtotal $93.72

## November 2015

Item | Quantity | Sum Cost
Female Mono Sockets | 10 | $4.66
3ft Mono Cables | 11 | $14.82

Subtotal $19.48

## February 2016

Item | Quantity | Sum Cost
3" PVC Cap | 2 | $7.96
4" PVC Cap | 2 | $15.90
Spring Doorstop | 6 | $11.82
Cherry Mx switches | 50 | $30.00
Assorted Bolts | 100+ | $44.44
JST Connectors | 200 | $13.98
4x8' 1/8" Acrylic Sheet | 1 | $132.32
2x4' 3mm Plywood | 2 | $12.00

Subtotal $268.42

## March 2016

Item | Quantity | Sum Cost
Assorted HomeDepot Hardware | X | $49.55

Subtotal $49.55

## April 2016

Item | Quantity | Sum Cost
Printed Poster | 1 | $39.24
Poster Frames | 2 | $20.78

Subtotal $39.24

## Product Cost Estimate

AT Keyboard—$41.50 | Cost | AT Button—$9.00 | Cost
16 x Cherry MX Switches 2’ x 4’ Plywood 2 x Handles 1 x MSP430F5529 | $16.00 $6.00 $10.00 $12.00 | 1 x Cherry MX Switch 1 x 3.5mm Mono 0.3kg PLA | $1.00 $0.50 $7.50

# Global and Societal Impact of Project

We have reviewed the environmental impact of this project to be negligible. Components of the system are all readily available for purchase in the United States and have passed all pertinent consumer regulations. Hardware, when discarded, should be disposed of based on the relevant regulations.

Security vulnerabilities can be introduced when a person decides to build our design with modifications to the microcontroller firmware. Since many existing keyboard kits available on the market use similar microcontrollers and firmware approaches, this keyboard is adequately secure in respect to the scope of modern keyboards. Our project is open source, and if another person was to use our design and implement a key logger into the source code for the keyboard, they could potentially steal information inputted by another user. We plan to counteract this possibility by providing source and binary checksums while requesting all potential developers build the project directly from source or from a trusted authority.

We are designing our hardware to be interoperable to conform to existing standards (USB 1.1, 2.1 CDC and HID). Legacy and emerging computer systems should allow for the keyboard to be operational via the USB interface.

With respect to personal privacy, our prospective desktop software design plans be a learning program that will remember most commonly used phrases in order to help predict the user’s word input and sentences. We will have to take ethical measures to ensure the raw or generated data taken is with consent and not distributed to unauthorized parties. We will also review later designs to implement fuzzing techniques which prevent the extraction of valid writings and communique of the user.

Health and safety concerns are minimal; the keyboard is constructed of nontoxic material. As far as the development of our product, we are prototyping with a chemical laser bed and we have to ensure proper ventilation and eye protection is used during operation. The 3D printers are printing with polylactic acid (PLA) thermoplastics that are food grade, thus posing limited risk and no noxious fumes during extrusion. Furthermore, we are soldering with leadless solder and are ensuring that proper safety measures are taken in the lab.

In regard to regulatory and legal issues, we are using MSP430 TI USB API Stack which includes the driverlib package. Both are clearly licensed under BSD compliant licenses via the following [9]. MSP430 hardware is subject to export restrictions for certain packages, but we are not crossing state or country lines and are not mailing the hardware systems.

In the end, systems are often victim to aging technology because the rapid innovations in technology for able bodied people—for example, systems developed a decade ago were not modified for high speed USB connections or flat panel monitors. Many of these old technologies are still in use today because they have no replacement or are prohibitively expensive to exchange. While the US does have programs that allow people who need AT, not everyone around the world has access to proper government programs and health insurance that will offset the costs. The project will aim to prioritize the safety and affordability of the users.

# Future Work

The AT Keyboard came a long way over the past two semesters, but there were several tasks and aspects we did not investigate as fully as we wished to. The keyboard has recently been redesigned to have eight switches per paddle with a different character mapping. This new design should undergo more stringent user testing and review. Additionally, we are interested in supporting both MSP430 and Atmel microcontrollers as the driver for the keyboard; currently only the MSP430 has working firmware.

Our AT Button design reached a fairly stable point before the end of the semester. There is still much room for expansion on the idea (such as into wireless capabilities) and manufacturing methods (laser cut, CNC, etc).

# Conclusion

Solutions available are expensive and difficult to obtain. There is a distinct need for human interface devices which meet many AT requirements and are available to wider audiences for more reasonable cost. The most significant differences between competing products versus our product is the low price. We strive to encourage others to create and publish an open source product that will allow people develop custom, low cost AT wherever a makerspace is available. Ultimately, the goal was to lay the groundwork for better availability of AT HID devices for the future.

Appendix A

## User’s manual - AT Keyboard

In the most recent design, the AT Keyboard consists of a few major components: the mounting backplane, two 8-key paddles, and an MSP430 microcontroller launchpad. The end design of the AT Keyboard will include an ATmega microcontroller, but should be functionally identical.

To use the AT Keyboard, simply plug in a USB-micro cable to both the keyboard and a host computer. The keyboard will automatically enumerate as a HID keyboard to the host computer, and should now be active for typing.

Begin with both paddles centered in their default state.

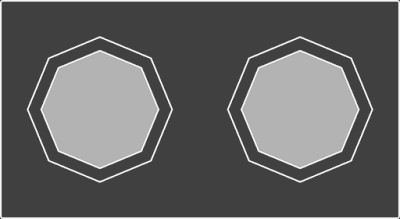
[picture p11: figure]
view

Move the left paddle to select a grouping of characters.

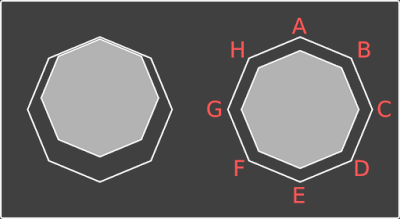
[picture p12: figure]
view

Keeping the left paddle pressed against the corner, move the right paddle to select and type a character.

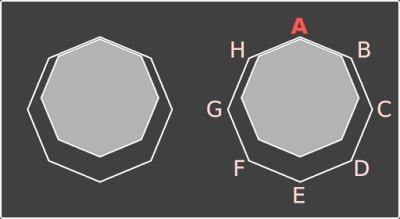
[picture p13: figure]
view

To type the next character, first release or guide both paddles back to the center of their octagon, then repeat the group and character selection.

## User’s manual - AT Button

The AT Button in earlier releases came with a separate 3.5mm male to male mono cable. Newer versions include the cable as an integrated component of the button. All versions should be otherwise interoperable.

To use the AT Button, first locate and configure a device capable of accepting a 3.5mm momentary switch input. The button is designed to accept multiple base materials, and can have a rubber base to be set on a flat desk-like surface, a velcro base to be mounted to a velcro surface, or a bolt-hole pattern to be bolted to a receiving plate. Once attached and oriented for the user, plug the button into its receiving device and use as you would any commercially available assistive touch button.

## User’s manual - Predictive Software

The predictive text plugin is available for Chromium browsers. To use, install from the Chrome App Store (note: plugin is not yet available, on the Chrome App Store). While typing, the plugin will monitor text input and provide suggested auto-completions.

# Appendix B - External Resources

[1]

http://www.ncbi.nlm.nih.gov/pmc/articles/PMC1475175/?page=1

[2]

http://www.atmel.com/tools/AT90USBKEY.aspx

[3]

https://www.obdev.at/products/vusb/index.html

[4]

https://www.obdev.at/products/vusb/index.html

[6]

http://reprap.org/wiki/Printrbot

[7]

http://www.thingiverse.com/thing:591674

[8]

https://www.hotends.com/index.php?route=product/product&path=68&product_id=88

[9]

http://software-dl.ti.com/msp430/msp430_public_sw/mcu/msp430/MSP430_USB_Developers_‌Package/latest/index_FDS.html

ADAPTIVE HID21

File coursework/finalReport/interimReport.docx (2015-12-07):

Adaptive H.I.D.


https://github.com/ctag/cpe495


CPE 495 Interim Report

Fall 2015

University of alabama in huntsville

301 Sparkman Dr. NW, Huntsville, Alabama 35899

Christopher Bero

Bryant Johnson

Michael Baldwin
John Gould

Project Summary

Design a set of adaptive interface devices for modern computers with readily available consumer machinery and products. The product will have a focus on affordability, iterative design, and easy operation. Construct and test the devices for viability in general use; then generate a case study on the effectiveness of this approach to bringing adaptive technology to a larger audience.

Team Description

The Adaptive H.I.D. project was envisioned to develop affordable computer interface devices and bring adaptive technology to more people around the world. Each team member was selected based on how their personal expertise would benefit the project.

Chris Bero is the Hardware Lead for the project with the subtask of community outreach. He originally conceptualized the project after noticing the many shortfalls of adaptive technology in his free time and drafted multiple designs that could benefit the disabled community. He is very knowledgeable in microcontrollers, 3D printers, and collaborative software development.

Michael Baldwin is the Software Lead for the project. He leads the pursuit in either upgrading an existing package or creating our own custom keyboard interface which uses predictive text to lessen the number of characters required to complete a word. Michael has a very strong programming background and implements professional modern style when developing code.

Bryant Johnson is the Testing Lead with the subtask of technical writer. He is responsible for creating the unit tests and maintaining the documentation of the entire project. He excels in strategizing the project and rationalizing each process while paying attention to fine details. His interest include cybersecurity and reverse engineering.

John Gould is the Systems Lead for this project. He is responsible for integration of the hardware and software that will be developed for this project and will ensure that the mechanical elements will work together in the finished product. His strengths include microcontroller based projects and software development.

In the event that one of our team members will not be able to complete their assigned duties, the responsibility of the lost member will be divided among the remaining members for the rest of the course. Additionally, all members assist and aid in other duties when available.

Introduction

Our team is researching and building Adaptive Technology human interface devices to help people living with disabilities interact with computers. Adaptive technology (AT) is a device or component which is specifically designed for persons with disabilities. Human Interface Devices (H.I.D) is a method by which a human interacts with an electronic information system either by input or output. Computers have dropped in price, grown in capability, and leapt into consumer markets in the past few years. Adaptive Technologies which help persons living with disability interface with a computer have been left behind in this regard. Solutions available are expensive and difficult to obtain. There is a distinct need for human interface devices which meet many AT requirements and are available to wider audiences for more reasonable cost. This project is going to be a student lead and noncommercial in nature. We wish to make clear that our design decision to present the project as open source incurs additional work for us to have a clean operating environment that others can approach and utilize in separate projects, not a sidestepping of features we do not intend to implement. We are developing two keyboard interfaces that include a Sliding Keyboard, and a Brailling Keyboard. The sliding keyboard will require no finger movement to type characters, instead utilizing shoulder and elbow ranges. Our brailling keyboard will consist of the standard eight button brailling interface, but made with consumer level material at a lower price. We are interfacing with local disability service groups United Cerebral Palsy (UCP) of Huntsville and National Federation of the Blind (NFB) of Huntsville.

We established our marketing and engineering requirements based upon UNICEF’s World Report on Disability. UNICEF states, “Manufacturing or assembling [AT] products locally, using local materials, can reduce cost and ensure that devices are suitable for the context.” Priority of the design was for cheap and readily available materials and techniques—allowing for the product to be easy to build and modify. Consumers should be able to with relative ease assemble the device themselves. Additionally we wanted to build a product with equivalent or better functionality without increasing complexity of user interaction. The design should be durable and adhere to the standards of current AT marketable solutions. The Marketing Requirements are as follows:

- Open Source Design
  - Require only items available to common makerspaces
  - Easy to iterate and customize
  - Low cost requirements for parts and machinery
- Easy to Operate
  - Must provide as good or better functionality than existing solutions
- Reliable
  - Must accept improper input and have a robust mechanical design.

The Engineering Requirements were based upon current mechanical keyboard design standards. We needed the hardware to react to changes under 6 milliseconds while in use. Each switch will need to last at least 10 Million cycles while supporting at least 30 words per minute operation at 90% accuracy. The device should be operational from -10 Degrees Celsius up to 70 Degrees Celsius. These requirements are typically found on the product speciation section of modern mechanical keyboards by various brands on the marketplace. Research was conducted by browsing and comparing specifications of listed items in retail stores.

Background

There are many shortfalls when it comes to AT. The main issue is that there is high development costs to a low volume market. Existing products include a Large Switch Keyboard which is aimed towards people with motor disabilities and lack of precision. It is less costly but does not necessarily solve the problem just lessens the possibility of error. Maltron created a Braille embossed keyboards have the same complexity of a regular keyboard, just using a simple mapping to the existing format, however it is very costly and less efficient. Additionally, there have been various projects that aimed to solve some challenges that disabled people may face when using technology. The Audrey Braille Display was an attempt to create a low cost braille refreshable display however the concept was abandoned in 2012. Ferrofluid Braille Displays were conceptualized to use electromagnetics however it was found to be very expensive. The most significant differences between competing products versus our product is the low price and iterative design. We strive to create and publish an open source product that will allow people develop custom, low cost AT wherever a makerspace is available.

Trade-off Analysis of Design Alternatives

Various alternative products were considered in the design of this project. We have reviewed the possibility of creating four different systems to be part of our suite of low cost AT devices that we will deliver as the outcome of our project. With our trade-off analysis we investigate the options available for our project and the design decisions which lead to our chosen systems.

Products

Within the project of creating AT HID, our team generates several product ideas and needs to decide which are worth pursuing and how to go about designing the results.

Sliding keyboard. Our first product is a keyboard to limit the required dexterity of typing. Targeted at users with conditions commonly associated with amyotrophic lateral sclerosis or cerebral palsy, this keyboard removes keys from the user’s path and instead places two horizontal “pucks” down as control surfaces. Pucks can be a custom design from a handle to a joystick, anything that the user can operate to slide the base of the puck around an inset hexagon that it resides on. At each corner of the hexagon are mechanical switches, totaling twelve between the two pucks. If each puck is moved to contact a switch, then depending on the key map a range of either 36 or 72 characters can be represented.

RFB. The next product we discuss is a braille refreshable display. Targeted at users with low or no eyesight, this system has two design proposals, one which uses a rack and gearing system to exchange templates of braille, and one which uses electro-cutaneous feedback to represent raised braille dots. The geared system would be based on a concept design named ‘Audrey’ (http://www.utopiamechanicus.com/article/open-source-hardware-braille-display/) from David Pankhurst. This approach uses a rack with one half of a braille character enumerated along it from a single dot to all four; several racks are placed side by side to create braille characters. A stepper motor is then rotated beneath the racks and slides them to spell braille characters. The electro-cutaneous method would consist of a PCB with a row of braille dots in the form of unsoldered contacts. These contacts would then push a small amount of current through a hand passing over them to interact with cutaneous sensors in the skin and create the sensation of an edge below the finger to correspond with braille.

Brailler. Complementing braille output is a brailling keyboard for input to a computer. Braillers used to be mechanical counterparts to typewriters and would physically press braille dots into paper; present day braillers are considered a subset of the chordal keyboarding arena, where multiple keys are pressed at once to indicate a word -- rather than a sequence of keys pressed one at a time. Braillers can be found as standalone items or bundled with a refreshable braille display to provide the complete loop of input and output from a computer. Our approach is to recycle design decisions from the sliding keyboard and apply them to the similarly functioning brailler in order to create a device that is easy to make and more affordable than current market options.

AT Button. While our customer expressed general interest in the above solutions, we also learned a lot about the current state of AT in use at UCP and received enough direction to build out our case study plan for more AT. One of the more common systems for actuation in use at UCP are SPST buttons -- roughly four inch diameter pads -- that terminate to a 3.5mm mono audio pole. These buttons are then plugged into a variety of host items in order to provide a greater ease of access to the item. At UCP a conflict has occurred where the market price for these buttons is high -- in the $60 to $80 range -- and their use level is low -- an example is sub $20 toy adapting. We suspect this is caused by the quality of the buttons, if the button is associated with a device to request food or water, then it must work each and every time. Toy adapting isn’t quite as mission critical though, and a solution which provides “button to 3.5mm jack” at a lower price would be ideal. Thus we intend to investigate using mechanical keyboard switches with thermoplastic or acrylic cases to create more affordable actuation devices and test them as part of our case study.

Switch Circuits. For switches, we will use port inputs on either the MSP430 or atMega and arrange switches with pulldown resistors.

Our plan is to implement a scanning grid for the switches as used in CPE322 for FPGAs.


For testing our firmware and hardware approach, we constructed a set of twelve isolated switches which can be wired into breadboards. The tradeoff here is ease of configuration in exchange for a lot of tidiness.


Material breakdown for both keyboards

We’re following Design Analysis from the University of Delaware’s Nonprofit Management Certificate Course (http://www.udel.edu/ccrs/NPMCC_2006_Materials/Tradeoff_Analysis_Example.pdf).

For our design decisions, we hold the brailling keyboard and sliding keyboard to have similar enough hardware qualities as to occupy the same space of design approaches. Hardware approaches were based on components that we have had previous experience with, could easily source, and knew to have high availability in common makerspaces (PLA printing, 30W laser CNC bed).

Design Scenario A

- MSP430F5529 processor
- Cherry Corp. MX switches
- Thermoplastic case

Design Scenario B

- MSP430F5529 processor
- Gatereon switches
- Laser cut case

Design Scenario C

- ATmega328p processor
- Cherry Corp. MX switches
- Thermoplastic case

Design Scenario D

- ATmega328p processor
- Gatereon switches
- Laser cut case

Each approach’s set of decision criteria is given an importance magnitude 1-5 and instance rating 1-5. The resulting grade ( = importance * rating) is assigned and reviewed alongside functional or behavioral decompositions.

Scenario A - Decision Criteria | Importance | Rating | Grade
Production Cost | 5 | 3 | 15
Component Availability | 4 | 2 | 8
Assembly Skill/Time | 4 | 3 | 12
System Durability | 3 | 4 | 12
Design Complexity | 2 | 3 | 6
Grade total | | | 53

Scenario B - Decision Criteria | Importance | Rating | Grade
Production Cost | 5 | 5 | 25
Component Availability | 4 | 4 | 16
Assembly Skill/Time | 4 | 4 | 16
System Durability | 3 | 2 | 6
Design Complexity | 2 | 4 | 8
Grade total | | | 71

Scenario C - Decision Criteria | Importance | Rating | Grade
Production Cost | 5 | 2 | 10
Component Availability | 4 | 3 | 12
Assembly Skill/Time | 4 | 4 | 16
System Durability | 3 | 4 | 12
Design Complexity | 2 | 4 | 8
Grade total | | | 58

Scenario D - Decision Criteria | Importance | Rating | Grade
Production Cost | 5 | 4 | 20
Component Availability | 4 | 5 | 20
Assembly Skill/Time | 4 | 5 | 20
System Durability | 3 | 2 | 6
Design Complexity | 2 | 4 | 8
Grade total | | | 74

Analysis factors

- Cherry Corp. products are often difficult to source, are more expensive than Gatereon compliments.
- Grading thermoplastic and laser laminate cases is difficult due to the vast plethora of available systems and operator knowledge. We settled on as unbiased a format as possible, with plastic cases offering better system durability and longevity with a higher complexity and design cost.
- The two microcontrollers compared here were chosen either for their popularity in crowd-designed keyboards (such as the Kiibohd Infinity) or their use in previous UAH courses (CPE323).
- We tried to favor availability and assembly factors heavily in this stage, as a durable and cheap system is unhelpful if nobody is willing or capable to generate them for people in need.

Although the Atmel/Gatereon solution provided the best score by our criteria, our team did not have a “will fetch a good grade” section. This unfortunately ended up being the deciding factor, and we chose to investigate the msp430/cherry/thermoplastic option as it used microcontrollers presented in a previous UAH class and promised a higher level of complexity. We wonder how often this happens in the real world.

Response to Feedback

As a result of the CPE 495 Project Proposal Presentation to our peers and instructors, we received valuable feedback. We outlined and addressed each of the comments and concerns below.

Sounds like a useful/feasible project. But is it Valuable to the impaired customer?

We can draw some confidence of the project value from the presence of existing items on the market. Our sliding keyboard is not a new concept, but we are working to make a key-less keyboard easier to obtain.

Value is difficult to determine. Take for example voice input and output; voice recognition and synthesis software has become quite capable lately and we have witnessed a lot of similar comments to yours online about the need to physical AT devices. To clarify our stance, imagine an office setting in which a voice system is the only method available for someone to interact with a computer. Not only does eight hours of talking sound appallingly strenuous, but the situation may also be distracting for others working nearby. The need for a variety of options exists because there is not a single best solution to aiding a person living with disability in using a computer.

Suggested additions - audio shortcuts - or some other non-tactile method, may add large value at small costs.

Thank you for your input, we have reviewed it as a component of prospective designs. Refer to the above question for our reasoning for not pursuing this.

The idea of reducing the cost of current keyboard is nice and suitable. However, I was not able to recognize how the cost will actually be reduced. The proposal presentation looks to be vague. It would be better to present more specifically the cost reduction.

Please see Introduction (page 1) in which we discuss our plan to use consumer grade materials with existing manufacturing infrastructure to generate an affordable alternative.

We recognize the comment on a vague proposal. This was in part due to our ongoing research for solutions and existing systems, as we did not wish to commit to something that would be usurped the next day. We will strive to make all future correspondence and presentations as well balanced in details available to us and time.

Very informative presentation. I was able to follow everything without any prior knowledge in the field. My only suggestion would be to see about locating a working pre-existing solution (braille keyboard) that you can access to be able to test against. Perhaps contact one of your disability advocates and see if they have a disabled-accessible computer lab with some of the hardware available so no one has to purchase a new one.

We agree and wish to pursue this. Our customer, UCP, has a few solutions which we can request access to, although we have yet to locate a brailling keyboard or RFB to borrow.

How will you make the determination that the product you produce is easy to use by the customer? Need a specific plan and customer.

Please see Test Plan (page 10) in which we discuss our intent to perform a case study and see if our affordable solution measure desirably against market solutions. Thanks for bringing the need of a customer to our attention, we have since located one.

Global and Societal Impact of Project

We have reviewed the environmental impact of this project to be negligible. Components of the system are all readily available for purchase in the United States and have passed all pertinent consumer regulations. Hardware, when discarded, should be disposed of based on the relevant regulations.

Security vulnerabilities can be introduced when a person decides to build our design with modifications to the microcontroller firmware. Since many existing keyboard kits available on the market use similar microcontrollers and firmware approaches, this keyboard is adequately secure in respect to the scope of modern keyboards. Our project is open source, and if another person was to use our design and implement a key logger into the source code for the keyboard, they could potentially steal information inputted by another user. We plan to counteract this possibility by providing source and binary checksums while requesting all potential developers build the project directly from source or from a trusted authority.

We are designing our hardware to be interoperable to conform to existing standards (USB 1.1, 2.1 CDC and HID). Legacy and emerging computer systems should allow for the keyboard to be operational via the USB interface.

With respect to personal privacy, our prospective desktop software design plans be a learning program that will remember most commonly used phrases in order to help predict the user’s word input and sentences. We will have to take ethical measures to ensure the raw or generated data taken is with consent and not distributed to unauthorized parties. We will also review later designs to implement fuzzing techniques which prevent the extraction of valid writings and communique of the user.

Health and safety concerns are minimal, the keyboard is constructed of nontoxic material. As far as the development of our product, we are prototyping with a chemical laser bed and we have to ensure proper ventilation and eye protection is used during operation. The 3D printers are printing with polylactic acid (PLA) thermoplastics that are food grade, thus posing limited risk and no noxious fumes during extrusion. Furthermore, we are soldering with leadless solder and are ensuring that proper safety measures are taken in the lab.

In regard to regulatory and legal issues, we are using MSP430 TI USB API Stack which includes the driverlib package. Both are clearly licensed under BSD compliant licenses via the following [http://software-dl.ti.com/msp430/msp430_public_sw/mcu/msp430/MSP430_USB_Developers_‌Package/latest/index_FDS.html]. MSP430 hardware is subject to export restrictions for certain packages, but we are not crossing state or country lines and are not mailing the hardware systems.

In the end, systems are often victim to aging technology because the rapid innovations in technology for able bodied people—for example, systems developed a decade ago were not modified for high speed USB connections or flat panel monitors. Many of these old technologies are still in use today because they have no replacement or are prohibitively expensive to exchange. While the US does have programs that allow people who need AT, not everyone around the world has access to proper government programs and health insurance that will offset the costs. The project will aim to prioritize the safety and affordability of the users.

Test Plan

Primary testing will be dependent on the cooperation of outside organizations. Optimally we would like to allow several people from our target audience to try several of our prototypes so we can determine values such as words per minute and get feedback on the system for improvements. Our proposed test plan includes unit tests on each of the essential hardware elements. This includes testing the hardware for durability during operation. Additional tests will be the software’s predictive text ability.

Integration tests will be performed to observe the hardware and software modules as a group. For example, to ensure a proper data sync we must compare switch input versus the data output. Extensive integration tests must also be qualitative based on customer response. The device will be tested based on the ease of use and comfort.

Acceptance tests will use the feedback from the customers at UCP of Huntsville. With the help of outside organizations we would like to allow users in need of our device to actually try the device themselves and return their feedback for the majority of our testing. Without this support we will still be running similar tests but with group members instead.

CPE 495 Go/No Go Milestone(s)

We have successfully met our milestone that was set forth and approved by instructor. We were able to identify UCP of Huntsville as a valid customer that was willing to evaluate the effectiveness of the project. We had made substantial research and provided documentation on what approaches worked well and would be worth further investigation in future projects. We managed to create a physical input device as a proof of concept that will be further improved upon in the upcoming month. Finally, we broke ground on our software package with prospective solutions.

CPE 496 Course Team-Specific Deliverables

Our course deliverables are twofold. We are providing our instructor with the systems designed during the class, along with our case study on the viability of this approach to manufacturing. This includes working prototypes of input devices for the handicapped. We will include a collection of software enhancing prototypes from a simple I/O peripheral to a more useful tool such as predictive text. Additionally, we are providing the physical systems to a local benefactor, either UCP or NFB of Huntsville. Ultimately, the goal is to have other people become interested in creating Adaptive Technology.

CPE 496 Project Work Breakdown Structure and Base Line Project Schedule

We have outlined the project schedule using the GanntProject. For this semester we have been on time with each step in the development process and plan to remain on track for Spring 2016.

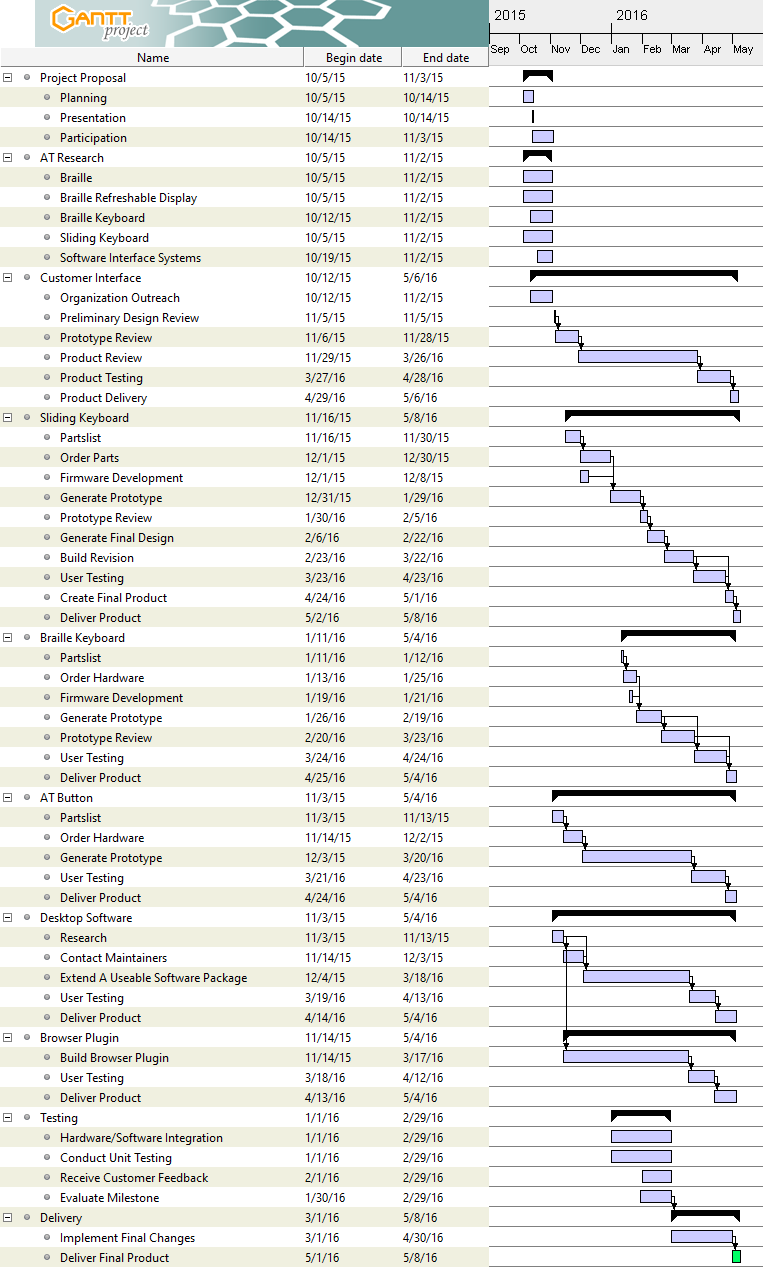
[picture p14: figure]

CPE Professional and Ethical Statements of Responsibility

Each student within the Adaptive H.I.D project team (Christopher Bero, Michael Baldwin, Bryant Johnson, and John Gould) hereby reaffirm our commitment to the common good of the Adaptive H.I.D. team. Additionally, we will continue to adhere to the policies of UAH and the ethical responsibilities assumed by adherence, as well as throughout the scope of the CPE 496 project.

CPE 496 Project Cost Evaluation

We do not anticipate the need to purchase any additional components for CPE 496. Any additional items we may need will either be 3D printed, of minimal cost, or already available through the makerspace available resources.

Conclusions

Our CPE 495 design experience was extensive in researching the pros and cons of developing each system. We were able to select what specific parts and designs we would pursue for the following Spring 2016 semester. The primary obstacle for CPE 496 will be product testing and optimizations after the initial prototype. We will have to coordinate multiple sessions with our customer in order to deliver the best possible product on time.

Regarding individual technical strengths and weaknesses, our group’s core proficiencies allow us to bond each essence of project development. Each team member provides knowledge from their area of expertise. The primary weakness of our group is time management. The responsibility of a job, compounded by the demands of a class schedule, created stress and feelings of being overwhelmed while making the group as a whole feel awkward when meeting schedules are discussed. We utilized options which include online instant messengers, such as Google Hangouts, to offset the problem in order to facilitate communication. For the remainder of the project, we do not foresee any technical difficulties. If we to adhere to the schedule that we have developed, we will be able to successfully deliver our product.

Appendix A: Copy of Progress Reports

## Progress Report 1

Class | Week
CPE 495 | 5 Oct. 2015 - 9 Oct. 2015

### Adaptive H.I.D.

- Christopher Bero
- Bryant Johnson
- John Gould
- Michael Baldwin

### Project Status

Since the course launch, we have:

- Formed a team
- Reviewed candidate projects.
- Selected a project for milestone 1 attempt.
- Begun initial research on necessary background and design.

### Difficulties Encountered

As a team we've struggled to decide on a primary project. After several iterative reviews we've adjusted the initial keyboard project to increase scope of research and design.

### Next Sprint

For the next reporting period we intend to

- Complete and present a project proposal.
- Continue research on hardware and software design requirements.
- Begin construction of a parts list for hardware designs.
- Triage hardware designs to choose a spearhead for milestone 1's prototype.
- Begin setup of a hardware workbench to include a machine with adaptive programs installed for testing.

## Progress Report 2

Class | Week
CPE 495 | 12 Oct. 2015 - 16 Oct. 2015

### Adaptive H.I.D.

- Christopher Bero
- Bryant Johnson
- John Gould
- Michael Baldwin

### Project Status

- Attempted to contact organizations that are relevant to our product for testing and feedback (UCP NFB UAH DSS ADIB).
- We have gotten response from UCP and UAHDSS.
- Prepared purchasing guidelines for prototype materials.
- Gave project presentation to the class.
- Updated scope of projected, adjusted long term goals in case of difficulty.

### Difficulties Encountered

Firmly establishing contact has been slower than anticipated. The biggest criticism from the presentation was our lack of contact with potential customers. We have increased efforts of contact, with mixed results.

### Next Sprint

For the next reporting period we intend to:

-Begin investigation into the software aspect of the project. -Order materials for construction of the prototype. -Assess any changes to project details based on presentation

## Progress Report 3

Class | Week
CPE 495 | 19 Oct. 2015 - 23 Oct. 2015

### Adaptive H.I.D.

- Christopher Bero
- Bryant Johnson
- John Gould
- Michael Baldwin

### Project Status

We are currently waiting feedback from our presentation in order to move forward. We are creating our purchase order and continuing our attempt to contact groups who have already done relevant research in Adaptive Technology.

### Difficulties Encountered

Two of our team members are in the Honors College, which requires a Project Director: "Whether you write a thesis or do a project, you must have somebody with whom you can work closely and who is an expert in your chosen field. You may wish to work with a professor with whom you previously took a class, your major advisor, or someone with whom you have been working in a lab, studio, or in clinical practice ... Generally the director should have at least a graduate degree in her or his field, and preferably the terminal degree in the relevant field."

Difficulties include finding a person that fits this criteria.

### Next Sprint

For the next reporting period we intend to

- Continue research on hardware and software design requirements.
- Triage hardware designs to choose a spearhead for milestone 1's prototype.
- Begin setup of a hardware workbench to include a machine with adaptive programs installed for testing.

## Progress Report 4

Class | Week
CPE 495 | 26 Oct. 2015 - 30 Oct. 2015

### Adaptive H.I.D.

- Christopher Bero
- Bryant Johnson
- John Gould
- Michael Baldwin

### Project Status

This week we were able to schedule a meeting with our customer, UCP. We will be meeting with an Assistive Technology Specialist. While meeting with the customer is our primary concern for the time being, some progress has also been made on software development. We are currently researching existing software for text prediction which can be used to increase functionality of both our product hopefully existing products already owned and used.

### Difficulties Encountered

We are still trying to find a Project Director to meet the requirements for our two team members who are in the Honors College. Prior to the meeting we have planned with UCP we have had no face-to-face contact with any of our customers yet which has severely hindered our understanding of our customer’s needs. This meeting should help resolve this hurdle.

### Next Sprint

For the next reporting period we intend to do the following:

Meet with UCP and finalize our initial requirements on our hardware. Begin building a prototype input device. Continue research and begin trying various open source software applications which predict the intended completion of a fragment of a word.

## Progress Report 5

Class | Week
CPE 495 | 2 Nov. 2015 - 6 Nov. 2015

### Adaptive H.I.D.

- Christopher Bero
- Bryant Johnson
- John Gould
- Michael Baldwin

### Project Status

This sprint we conducted a meeting to gather ideas and questions in anticipation of our meeting with UCP. On November 5th we met with Kate Moseley of TASC to receive a presentation on AT systems and initial design feedback for our project.

We've also received our first shipment of hardware to begin building the sliding keyboard prototype.

### Difficulties Encountered

Coordinating team meetings and efforts through this semester’s class schedule of 431/434/435/412 has proved troublesome. We will begin implementing an hour sign off sheet for the next sprint to increase our cohesion with the group's timeline.

### Next Sprint

Tentatively:

- Christopher Bero
  - Get set up with microcontroller hardware and begin circuit designs for sliding keyboard.
- John Gould
  - Work with Christopher Bero and Michael Baldwin to make sure the initial hardware and software systems are compatible from a systems view.
- Bryant Johnson
  - Continue work on tests for both hardware and software prototypes.
- Michael Baldwin
  - Finish software research and begin design phase for program MVP

## Progress Report 6

Class | Week
CPE 495 | 9 Nov. 2015 -- 13 Nov. 2015

### Adaptive H.I.D.

- Christopher Bero
- Bryant Johnson
- John Gould
- Michael Baldwin

### Project Status

This week we

- Used the information from our customer meeting to finish the Specifications and Requirements document.
- Began the Go/No Go hardware and software construction.

### Difficulties Encountered

- The MSP430 USB toolkit isn't compiling. We need to check with some dependencies to correct this.
- The open source software that we're investigating are difficult to break ground with. We need to follow up with them on mailing lists to get a scope of tasks involved in compiling current development builds.

### Next Sprint

- Christopher Bero:
  - Install MSP430 USB toolkit. Flash initial firmware tests.
- Michael Baldwin:
  - Work on contacting maintainers of open source projects.
- John Gould:
  - Help with bringing in software to the wiki.
- Bryant Johnson:
  - Continue work on tests for both hardware and software prototypes.

## Progress Report 7

Class | Week
CPE 495 | 16 Nov. 2015 -- 20 Nov. 2015

### Adaptive H.I.D.

- Christopher Bero
- Bryant Johnson
- John Gould
- Michael Baldwin
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

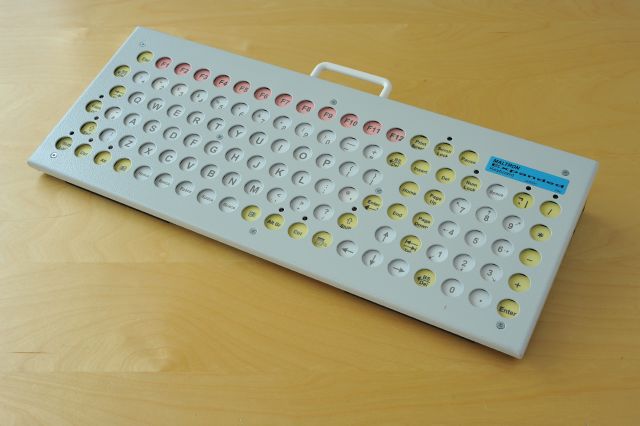
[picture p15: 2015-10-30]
coursework/proposal/images/large_keyboard.jpg

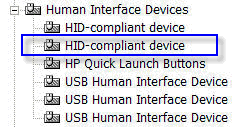
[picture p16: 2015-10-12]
coursework/proposal/images/hid_mouse.gif

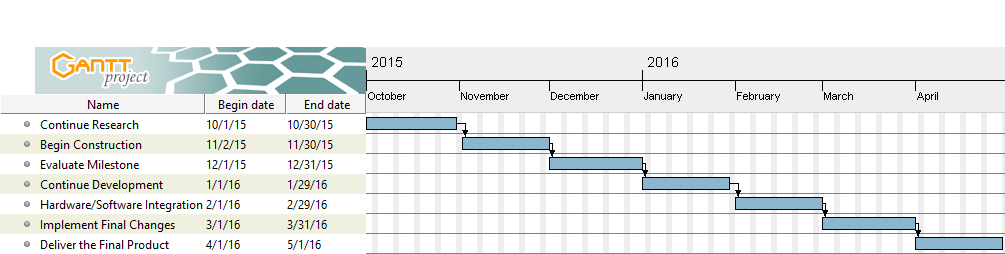
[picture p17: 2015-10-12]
coursework/proposal/images/GanttChart.png

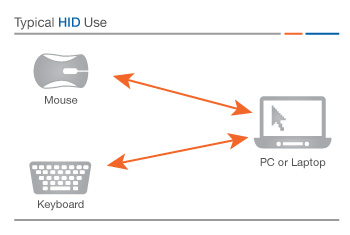
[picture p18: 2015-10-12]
coursework/proposal/images/HID.jpg

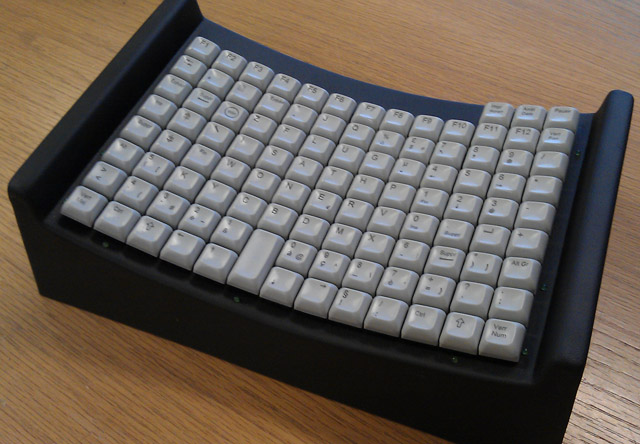
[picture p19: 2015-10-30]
coursework/proposal/images/head-mouth-stick-640px.jpg

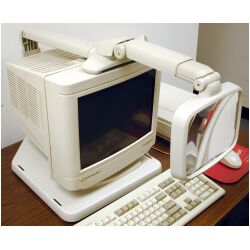
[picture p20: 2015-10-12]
coursework/proposal/images/screen_magnifier.jpg

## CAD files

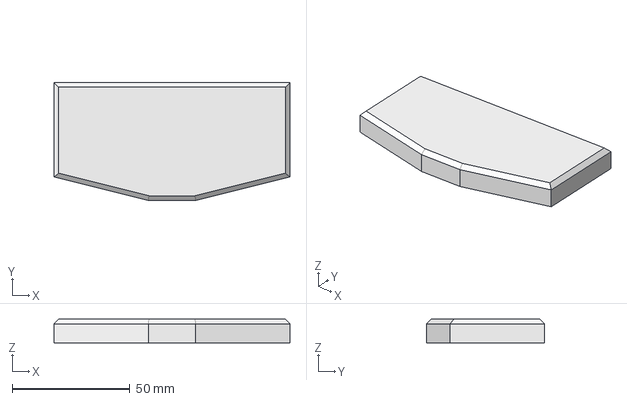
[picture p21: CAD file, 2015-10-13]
models/braille/braille.fcstd
100.0 x 50.0 x 10.0 mm

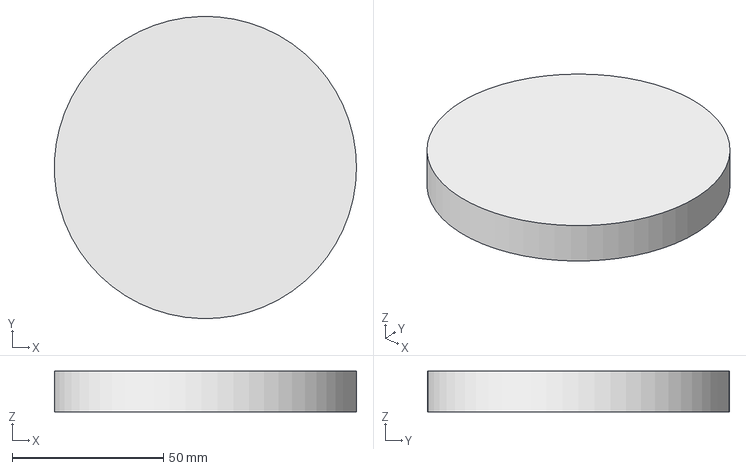
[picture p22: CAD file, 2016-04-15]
models/button/button_base.fcstd
99.9 x 100.0 x 13.5 mm

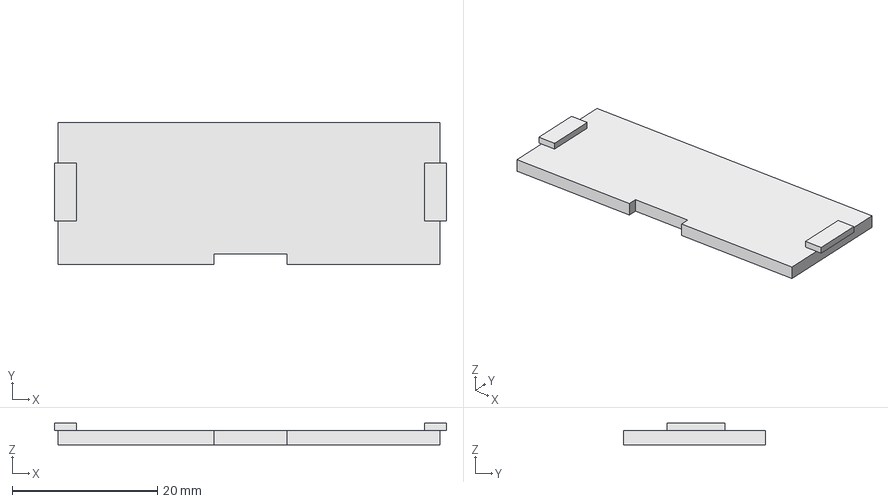
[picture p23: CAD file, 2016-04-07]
models/button/button_hatch.fcstd
54.0 x 19.6 x 3.00 mm

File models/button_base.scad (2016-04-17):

/*
 * Includes
 */
use <gcb_files/keyboards/cherry/keycap_mount.scad>;
use <gcb_files/arcade/cap.scad>;

$fn = 60;

base_height = 10;
base_diameter = 100;
bolt_count = 6;
rounding_radius = 3;

// thickness of the wall.
wall_thickness = 1;

// diameter of the plunger. ideally in mm
plunger_diameter = 80;

// height of the plunger. ideally in mm
plunger_height = 12;

// put a cross under the cap for reinforcement. it was done very quick and dirty just so you can add a better one if you need by looking at the code.
plunger_reinforcement = true;

module roundTop_cylinder(D, H, R) {
	//R = rounding_radius;
	difference() {
		minkowski() {
			cylinder(h=(H-R), d=(D-(R*2)), center=false);
			sphere(r=R);
		}
		translate([0,0,-R])
			cylinder(h=R, d=D);
	}
}

module switch_socket(H)
{
	clip_depth = 0.5;
	clip_width = 8;
	clip_height = 2;
	translate([0, 0, (H/2)]) {
		union() {
			cube([14, 14, H], center=true);
			for (r = [0:1]) {
				for (i = [-1:2:1]) {
					rotate([0, 0, r*90])
						translate([(i)*(7+(clip_depth/2)), 0, (H/2)-(clip_height/2)-1.75])
							cube([0.5, 8, 2], center=true);
				}
			}
		}
	}
}

module wire_channel()
{
	channel_length = 60;
	channel_diam = 3.5;
	channel_offset = 0.4;
	translate([(channel_length/2), 0, (channel_diam/2)+channel_offset]) {
		//cube([channel_length, channel_width, channel_diam], center=true);
		rotate([0, 90, 0]) {
			cylinder(h=channel_length, d=channel_diam, center=true);
		}
	}
}

module anti_warp(D, W, H)
{
	extra = (W*2);
	for (x = [-1:0.5:1]) {
		translate([0, x*((D/2)+W), (H/2)]) 
		cube([D+extra, W, H], center=true);
	}
	for (y = [-1:0.5:1]) {
		translate([y*((D/2)+W), 0, (H/2)]) 
		cube([W, D+extra, H], center=true);
	}
}

module bottom_threads(D, H)
{
	rotate([0, 0, 360/(bolt_count*2)]) { // Avoid collision with wire channel
		for (r = [0:(1/bolt_count):1]) { // 0->1 in fractions
			rotate([0, 0, r*360]) { // Spin item around origin
				translate([(base_diameter/2)-5, 0, (H/2)]) { 
					union() { // Join the cylinder and cone
						cylinder(h=H, d=D, center=true); // threads
						translate([0, 0, -((H/2)-2)]) { // cone to fit bolt head in
							cylinder(h=4, d1=(D*4), d2=D, center=true);
						}
					}
				}
			}
		}
	}
}

module button_base()
{
	difference() {
		cylinder(d=base_diameter, h=base_height);
		//roundTop_cylinder(base_diameter, base_height);
		switch_socket(base_height);
		wire_channel();
		anti_warp(base_diameter, 1, 0.4);
		bottom_threads(2.90, base_height);
	}
}

module button_retainer()
{
	_height = 6;
	_width = 9;
	difference() {
		roundTop_cylinder((base_diameter), _height, 2);
		cylinder(d=(base_diameter-(_width*2)), h=_height);
		cylinder(d=(base_diameter-((_width-3)*2)), h=_height-2);
		translate([0, 0, -3])
			bottom_threads(3, base_height);
	}
}




module button_cap(d, h, reinforcement){
	d=plunger_diameter;
	h=plunger_height;
	reinforcement=plunger_reinforcement;
	union() {
		difference() {
			plunger(d=d, h=h, concave=false);
			translate([0, 0, -8])
				cylinder(d1=30, d2=35, h=8);
		}
		translate([0, 0, (-8)]) {
			union() {
				mx_mount();
				if( true == plunger_reinforcement ) {
					translate([0,0, (wall_thickness/2) ]) {
						for (R = [0:1]) {
							rotate([0,0,R*90]) {
								difference() {
									cube([35,wall_thickness*3,wall_thickness], center=true);
									mx_mount_solid();
								}
							}
						}
					}
				}
			}
		}
		union() {
			if( true == plunger_reinforcement ) {
				translate([0,0, (wall_thickness/2) ]) {
					for (R = [0:1]) {
						rotate([0,0,R*90]) {
							difference() {
								cube([d,wall_thickness*3,wall_thickness], center=true);
								translate([0, 0, -(wall_thickness/2)])
								cylinder(d=35, h=wall_thickness);
							}
						}
					}
				}
			}
		}
		//translate([0, 0, -wall_thickness]) {
			difference() {
				cylinder(d=(d+(2*2)), h=wall_thickness);
				cylinder(d=d, h=wall_thickness);
			}
		//}
	}
}




module preview()
{
	color("blue") {
		button_base();
	}
	color("green") {
		translate([0, 0, base_height+2]) {
			button_retainer();
		}
	}
	color("red") {
		translate([0, 0, base_height+2]) {
			rotate([180, 0, 0]) {
				button_cap();
			}
		}
	}
}









//preview();
//button_base();
button_retainer();
//button_cap();

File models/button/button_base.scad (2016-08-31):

/*
 * Includes
 */
use <gcb_files/keyboards/cherry/keycap_mount.scad>;
use <gcb_files/arcade/cap.scad>;

$fn = 60;

base_height = 10;
base_diameter = 100;
bolt_count = 6;
rounding_radius = 3;

// thickness of the wall.
wall_thickness = 1;

// diameter of the plunger. ideally in mm
plunger_diameter = 80;

// height of the plunger. ideally in mm
plunger_height = 6;

// put a cross under the cap for reinforcement. it was done very quick and dirty just so you can add a better one if you need by looking at the code.
plunger_reinforcement = true;

module roundTop_cylinder(D, H, R) {
	//R = rounding_radius;
	difference() {
		minkowski() {
			cylinder(h=(H-R), d=(D-(R*2)), center=false);
			sphere(r=R);
		}
		translate([0,0,-R])
			cylinder(h=R, d=D);
	}
}

module switch_socket(H)
{
	clip_depth = 0.5;
	clip_width = 8;
	clip_height = 2;
	translate([0, 0, (H/2)]) {
		union() {
			cube([14, 14, H], center=true);
			for (r = [0:1]) {
				for (i = [-1:2:1]) {
					rotate([0, 0, r*90])
						translate([(i)*(7+(clip_depth/2)), 0, (H/2)-(clip_height/2)-1.75])
							cube([0.5, 8, 2], center=true);
				}
			}
		}
	}
}

module wire_channel()
{
	channel_length = 60;
	channel_diam = 3.5;
	channel_offset = 0.4;
	translate([(channel_length/2), 0, (channel_diam/2)+channel_offset]) {
		//cube([channel_length, channel_width, channel_diam], center=true);
		rotate([0, 90, 0]) {
			cylinder(h=channel_length, d=channel_diam, center=true);
		}
	}
}

module anti_warp(D, W, H)
{
	extra = (W*2);
	for (x = [-1:0.5:1]) {
		translate([0, x*((D/2)+W), (H/2)]) 
		cube([D+extra, W, H], center=true);
	}
	for (y = [-1:0.5:1]) {
		translate([y*((D/2)+W), 0, (H/2)]) 
		cube([W, D+extra, H], center=true);
	}
}

module bottom_threads(D, H)
{
	rotate([0, 0, 360/(bolt_count*2)]) { // Avoid collision with wire channel
		for (r = [0:(1/bolt_count):1]) { // 0->1 in fractions
			rotate([0, 0, r*360]) { // Spin item around origin
				translate([(base_diameter/2)-5, 0, (H/2)]) { 
					union() { // Join the cylinder and cone
						cylinder(h=H, d=D, center=true); // threads
						translate([0, 0, -((H/2)-2)]) { // cone to fit bolt head in
							cylinder(h=4, d1=(D*4), d2=D, center=true);
						}
					}
				}
			}
		}
	}
}

module button_base()
{
	difference() {
		cylinder(d=base_diameter, h=base_height);
		//roundTop_cylinder(base_diameter, base_height);
		switch_socket(base_height);
		wire_channel();
		anti_warp(base_diameter, 1, 0.4);
		bottom_threads(2.90, base_height);
	}
}

module button_retainer()
{
	_height = 6;
	_width = 9;
	difference() {
		roundTop_cylinder((base_diameter), _height, 2);
		cylinder(d=(base_diameter-(_width*2)), h=_height);
		cylinder(d=(base_diameter-((_width-3)*2)), h=_height-2);
		translate([0, 0, -3])
			bottom_threads(3, base_height);
	}
}




module button_cap(d, h, reinforcement){
	d=plunger_diameter;
	h=plunger_height;
	reinforcement=plunger_reinforcement;
	depth_offset=(plunger_height-2);
	// Overall item
	union() {
		
		// Main plunger body
		difference() {
			plunger(diameter=d, height=h, edge_radius=4);
			translate([0, 0, (-depth_offset)])
				cylinder(d1=30, d2=35, h=depth_offset);
		}
		
		// Lower support bars and mx socket
		*translate([0, 0, (-depth_offset)]) {
			union() {
				mx_mount();
				if( true == plunger_reinforcement ) {
					translate([0,0, (wall_thickness/2) ]) {
						for (R = [0:1]) {
							rotate([0,0,R*90]) {
								difference() {
									cube([35,wall_thickness*4,wall_thickness], center=true);
									mx_mount_solid();
								}
							}
						}
					}
				}
			}
		}
		
		// Upper support bars
		union() {
			if( true == plunger_reinforcement ) {
				translate([0,0, (wall_thickness/2) ]) {
					for (R = [0:1]) {
						rotate([0,0,R*90]) {
							difference() {
								cube([d,wall_thickness*4,wall_thickness], center=true);
								translate([0, 0, -(wall_thickness/2)])
								cylinder(d=35, h=wall_thickness);
							}
						}
					}
				}
			}
		}
		
		// Retainer lip
		difference() {
			cylinder(d1=d, d2=(d+(2*2)), h=3);
			cylinder(d1=40, d2=44, h=3);
		}
	}
}




module preview()
{
	color("blue") {
		button_base();
	}
	color("green") {
		translate([0, 0, base_height+2]) {
			button_retainer();
		}
	}
	color("red") {
		translate([0, 0, base_height+2]) {
			rotate([180, 0, 0]) {
				button_cap();
			}
		}
	}
}

module laser_base()
{
	difference() {
		circle(d=base_diameter);
		rotate([0, 0, 360/(bolt_count*2)]) { // Avoid collision with wire channel
			for (r = [0:(1/bolt_count):1]) { // 0->1 in fractions
				rotate([0, 0, r*360]) { // Spin item around origin
					translate([(base_diameter/2)-5, 0, 0]) { 
						circle(d=2.9); // threads
					}
				}
			}
		}
	}
}







//preview();
//button_base();
//button_retainer();
button_cap();
//laser_base();

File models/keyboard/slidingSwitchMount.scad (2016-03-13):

// Horizontal Mechanical Switch Mount
// Christopher Bero - csb0019@uah.edu
// CPE 496 - 2016

$fs = 1; // Minimum fragment size
interiorSize = 14; // Size of one side of the mounting hold for the switch
exteriorSize = 20; // Size of area around mounting hole
wallThickness = (exteriorSize - interiorSize)/2; // General wall thickness

// Area to be subtracted from the shell to make a mount point for the switch
module mountCavity()
{
    translate([0, wallThickness, wallThickness]) {
        cube([wallThickness, interiorSize, interiorSize]);
    }
}

// Exterior profile of the entire mount
module mountShell()
{
    holePlate=exteriorSize*2;
	holeDiam = 4;
	holeOffset = (wallThickness + (holeDiam/2));
    union() {
        *cube([wallThickness, exteriorSize, exteriorSize]); // Face plate
		translate([0, 0, (exteriorSize-wallThickness)])
			cube([exteriorSize, exteriorSize, wallThickness]); // Face plate
        // Shift bottom mounting plate
		translate([0, -((holePlate-exteriorSize)/2), 0])
            difference() {
                cube([exteriorSize, holePlate, wallThickness]); // Bottom plate
				// Distribute holes
				translate([holeOffset, holeOffset, 0]) {
					for (xi=[0:1]) {
						for (yi=[0:1]) {
							translate([xi*(exteriorSize-(holeOffset*2)), yi*(holePlate-(holeOffset*2)), 0])
							cylinder(wallThickness, d=holeDiam);
						}
					}
				}
            }
        cube([exteriorSize, wallThickness, exteriorSize]); // Right plate
        translate([0, exteriorSize-wallThickness, 0]) {
            cube([exteriorSize, wallThickness, exteriorSize]); // Left plate
        }
        *cube([]); // Mounting hole plate
    }
}

module antiWarp(X, Y, Z, buffer, rows, cols)
{
	width=((X-(buffer*2))/(cols*2));
	height=((Y-(buffer*2))/(rows*2));
	translate([buffer, buffer, 0])
	{
		for (xcount = [0:(cols-1)] )
		{
			for (ycount = [0:(rows-1)])
			{
				translate([xcount*(width*2), ycount*(height*2), 0])
					cube([width, height, Z]);
			}
		}
	}
}

difference() {
    mountShell();
    *mountCavity();
	antiWarp(exteriorSize+2, exteriorSize+2, 1.5, 1, 3, 3);
}



//minkowski() {
//	cylinder(h=wallThickness, r=2);
//	mountShell();
//}

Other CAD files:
models/keyboard/keyslider.fcstd
models/braille/base.fcstd
models/button/gcb_files/threads.scad
models/button/gcb_files/arcade/assembly.scad
models/button/gcb_files/arcade/cap.scad
models/button/gcb_files/arcade/cherry_mx_cap.scad
models/button/gcb_files/arcade/housing.scad
models/button/gcb_files/keyboards/cherry/keycap_mount.scad
models/button/gcb_files/keyboards/cherry/switch_mx.scad
models/button/gcb_files/torus.scad

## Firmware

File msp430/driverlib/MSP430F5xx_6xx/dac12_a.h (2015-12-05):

/* --COPYRIGHT--,BSD
 * Copyright (c) 2014, Texas Instruments Incorporated
 * All rights reserved.
 *
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
 * *  Redistributions of source code must retain the above copyright
 *    notice, this list of conditions and the following disclaimer.
 *
 * *  Redistributions in binary form must reproduce the above copyright
 *    notice, this list of conditions and the following disclaimer in the
 *    documentation and/or other materials provided with the distribution.
 *
 * *  Neither the name of Texas Instruments Incorporated nor the names of
 *    its contributors may be used to endorse or promote products derived
 *    from this software without specific prior written permission.
 *
 * THIS SOFTWARE IS PROVIDED BY THE COPYRIGHT HOLDERS AND CONTRIBUTORS "AS IS"
 * AND ANY EXPRESS OR IMPLIED WARRANTIES, INCLUDING, BUT NOT LIMITED TO,
 * THE IMPLIED WARRANTIES OF MERCHANTABILITY AND FITNESS FOR A PARTICULAR
 * PURPOSE ARE DISCLAIMED. IN NO EVENT SHALL THE COPYRIGHT OWNER OR
 * CONTRIBUTORS BE LIABLE FOR ANY DIRECT, INDIRECT, INCIDENTAL, SPECIAL,
 * EXEMPLARY, OR CONSEQUENTIAL DAMAGES (INCLUDING, BUT NOT LIMITED TO,
 * PROCUREMENT OF SUBSTITUTE GOODS OR SERVICES; LOSS OF USE, DATA, OR PROFITS;
 * OR BUSINESS INTERRUPTION) HOWEVER CAUSED AND ON ANY THEORY OF LIABILITY,
 * WHETHER IN CONTRACT, STRICT LIABILITY, OR TORT (INCLUDING NEGLIGENCE OR
 * OTHERWISE) ARISING IN ANY WAY OUT OF THE USE OF THIS SOFTWARE,
 * EVEN IF ADVISED OF THE POSSIBILITY OF SUCH DAMAGE.
 * --/COPYRIGHT--*/
//*****************************************************************************
//
// dac12_a.h - Driver for the DAC12_A Module.
//
//*****************************************************************************

#ifndef __MSP430WARE_DAC12_A_H__
#define __MSP430WARE_DAC12_A_H__

#include "inc/hw_memmap.h"

#ifdef __MSP430_HAS_DAC12_2__

//*****************************************************************************
//
// If building with a C++ compiler, make all of the definitions in this header
// have a C binding.
//
//*****************************************************************************
#ifdef __cplusplus
extern "C"
{
#endif

#include "inc/hw_regaccess.h"
//*****************************************************************************
//
//! \brief Used in the DAC12_A_init() function as the param parameter.
//
//*****************************************************************************
typedef struct DAC12_A_initParam
{
    //! Decides which DAC12_A sub-module to configure.
    //! \n Valid values are:
    //! - \b DAC12_A_SUBMODULE_0
    //! - \b DAC12_A_SUBMODULE_1
    uint8_t submoduleSelect;
    //! Selects the output pin that the selected DAC12_A module will output to.
    //! \n Valid values are:
    //! - \b DAC12_A_OUTPUT_1 [Default]
    //! - \b DAC12_A_OUTPUT_2
    uint16_t outputSelect;
    //! Is the upper limit voltage that the data can be converted in to.
    //! \n Valid values are:
    //! - \b DAC12_A_VREF_AVCC [Default]
    //! - \b DAC12_A_VREF_INT
    //! - \b DAC12_A_VREF_EXT
    uint16_t positiveReferenceVoltage;
    //! Is the multiplier of the Vout voltage.
    //! \n Valid values are:
    //! - \b DAC12_A_VREFx1 [Default]
    //! - \b DAC12_A_VREFx2
    //! - \b DAC12_A_VREFx3
    uint16_t outputVoltageMultiplier;
    //! Is the setting of the settling speed and current of the Vref+ and the
    //! Vout buffer.
    //! \n Valid values are:
    //! - \b DAC12_A_AMP_OFF_PINOUTHIGHZ [Default]
    //! - \b DAC12_A_AMP_OFF_PINOUTLOW
    //! - \b DAC12_A_AMP_LOWIN_LOWOUT
    //! - \b DAC12_A_AMP_LOWIN_MEDOUT
    //! - \b DAC12_A_AMP_LOWIN_HIGHOUT
    //! - \b DAC12_A_AMP_MEDIN_MEDOUT
    //! - \b DAC12_A_AMP_MEDIN_HIGHOUT
    //! - \b DAC12_A_AMP_HIGHIN_HIGHOUT
    uint8_t amplifierSetting;
    //! Selects the trigger that will start a conversion.
    //! \n Valid values are:
    //! - \b DAC12_A_TRIGGER_ENCBYPASS [Default]
    //! - \b DAC12_A_TRIGGER_ENC
    //! - \b DAC12_A_TRIGGER_TA
    //! - \b DAC12_A_TRIGGER_TB
    uint16_t conversionTriggerSelect;
} DAC12_A_initParam;

//*****************************************************************************
//
// The following are values that can be passed to the positiveReferenceVoltage
// parameter for functions: DAC12_A_init(); the param parameter for functions:
// DAC12_A_init().
//
//*****************************************************************************
#define DAC12_A_VREF_AVCC                                         (DAC12SREF_1)
#define DAC12_A_VREF_INT                                          (DAC12SREF_0)
#define DAC12_A_VREF_EXT                                          (DAC12SREF_2)

//*****************************************************************************
//
// The following are values that can be passed to the param parameter for
// functions: DAC12_A_init(); the amplifierSetting parameter for functions:
// DAC12_A_init(), and DAC12_A_setAmplifierSetting().
//
//*****************************************************************************
#define DAC12_A_AMP_OFF_PINOUTHIGHZ                                (DAC12AMP_0)
#define DAC12_A_AMP_OFF_PINOUTLOW                                  (DAC12AMP_1)
#define DAC12_A_AMP_LOWIN_LOWOUT                                   (DAC12AMP_2)
#define DAC12_A_AMP_LOWIN_MEDOUT                                   (DAC12AMP_3)
#define DAC12_A_AMP_LOWIN_HIGHOUT                                  (DAC12AMP_4)
#define DAC12_A_AMP_MEDIN_MEDOUT                                   (DAC12AMP_5)
#define DAC12_A_AMP_MEDIN_HIGHOUT                                  (DAC12AMP_6)
#define DAC12_A_AMP_HIGHIN_HIGHOUT                                 (DAC12AMP_7)

//*****************************************************************************
//
// The following are values that can be passed to the outputSelect parameter
// for functions: DAC12_A_init(); the param parameter for functions:
// DAC12_A_init().
//
//*****************************************************************************
#define DAC12_A_OUTPUT_1                                          (!(DAC12OPS))
#define DAC12_A_OUTPUT_2                                             (DAC12OPS)

//*****************************************************************************
//
// The following are values that can be passed to the submoduleSelect parameter
// for functions: DAC12_A_init(), DAC12_A_setAmplifierSetting(),
// DAC12_A_disable(), DAC12_A_enableInterrupt(), DAC12_A_disableInterrupt(),
// DAC12_A_getInterruptStatus(), DAC12_A_clearInterrupt(),
// DAC12_A_calibrateOutput(), DAC12_A_getCalibrationData(),
// DAC12_A_setCalibrationOffset(), DAC12_A_enableConversions(),
// DAC12_A_setData(), DAC12_A_disableConversions(), DAC12_A_setResolution(),
// DAC12_A_setInputDataFormat(), and
// DAC12_A_getDataBufferMemoryAddressForDMA(); the param parameter for
// functions: DAC12_A_init().
//
//*****************************************************************************
#define DAC12_A_SUBMODULE_0                                              (0x00)
#define DAC12_A_SUBMODULE_1                                              (0x10)

//*****************************************************************************
//
// The following are values that can be passed to the outputVoltageMultiplier
// parameter for functions: DAC12_A_init(); the param parameter for functions:
// DAC12_A_init().
//
//*****************************************************************************
#define DAC12_A_VREFx1                                                (DAC12IR)
#define DAC12_A_VREFx2                                                (DAC12OG)
#define DAC12_A_VREFx3                                                    (0x0)

//*****************************************************************************
//
// The following are values that can be passed to the conversionTriggerSelect
// parameter for functions: DAC12_A_init(); the param parameter for functions:
// DAC12_A_init().
//
//*****************************************************************************
#define DAC12_A_TRIGGER_ENCBYPASS                                 (DAC12LSEL_0)
#define DAC12_A_TRIGGER_ENC                                       (DAC12LSEL_1)
#define DAC12_A_TRIGGER_TA                                        (DAC12LSEL_2)
#define DAC12_A_TRIGGER_TB                                        (DAC12LSEL_3)

//*****************************************************************************
//
// The following are values that can be passed to the resolutionSelect
// parameter for functions: DAC12_A_setResolution().
//
//*****************************************************************************
#define DAC12_A_RESOLUTION_8BIT                                      (DAC12RES)
#define DAC12_A_RESOLUTION_12BIT                                  (!(DAC12RES))

//*****************************************************************************
//
// The following are values that can be passed to the inputJustification
// parameter for functions: DAC12_A_setInputDataFormat().
//
//*****************************************************************************
#define DAC12_A_JUSTIFICATION_RIGHT                               (!(DAC12DFJ))
#define DAC12_A_JUSTIFICATION_LEFT                                   (DAC12DFJ)

//*****************************************************************************
//
// The following are values that can be passed to the inputSign parameter for
// functions: DAC12_A_setInputDataFormat().
//
//*****************************************************************************
#define DAC12_A_UNSIGNED_BINARY                                    (!(DAC12DF))
#define DAC12_A_SIGNED_2SCOMPLEMENT                                   (DAC12DF)

//*****************************************************************************
//
// The following are values that can be passed toThe following are values that
// can be returned by the DAC12_A_getInterruptStatus() function.
//
//*****************************************************************************
#define DAC12_A_INT_ACTIVE                                           (DAC12IFG)
#define DAC12_A_INT_INACTIVE                                             (0x00)

//*****************************************************************************
//
// Prototypes for the APIs.
//
//*****************************************************************************

//*****************************************************************************
//
//! \brief Initializes the DAC12_A module with the specified settings.
//!
//! This function initializes the DAC12_A module with the specified settings.
//! Upon successful completion of the initialization of this module the control
//! registers and interrupts of this module are all reset, and the specified
//! variables will be set. Please note, that if conversions are enabled with
//! the enableConversions() function, then disableConversions() must be called
//! before re-initializing the DAC12_A module with this function.
//!
//! \param baseAddress is the base address of the DAC12_A module.
//! \param param is the pointer to struct for initialization.
//!
//! \return STATUS_SUCCESS or STATUS_FAILURE of the initialization process.
//
//*****************************************************************************
extern bool DAC12_A_init(uint16_t baseAddress,
                         DAC12_A_initParam *param);
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

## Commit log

2015-10-13 added models and project summary
    [base.fcstd, braille.fcstd, keyslider.fcstd]
2015-10-26 Uploading flowchart image for Software Wiki, also adding a new directory for similar future submissions.
2015-10-30 moved presentation files, migrated to camel case
2015-10-30 project proposal material
2015-11-10 Added TASC Powerpoint
2015-11-16 Adding workdivision table
    [Workdivision.ods]
2015-11-20 cleaned documents folder, added msp430 pdfs
    [Workdivision.ods]
2015-12-05 updated gitinore and Qtcreator screwed with files
2015-12-05 circuits for report
    [allSwitchesCircuit.fzz, switchCircuit_1.fzz]
2015-12-07 added debug switch image
    [debugSwitchesCircuit.fzz]
2016-01-26 laser template for keyboard
2016-01-28 created base file for switch mount scad
    [slidingSwitchMount.scad]
2016-01-28 switch mount something-something alpha is done
    [slidingSwitchMount.scad]
2016-02-08 added warp relief points
    [slidingSwitchMount.scad]
2016-02-12 added topical presentation powerpoint
2016-03-05 keyboard laser file for prototype 2
2016-03-13 updated sliding switch mount
    [slidingSwitchMount.stl]
2016-03-13 created testing button base
    [button_base_1.blend]
2016-03-13 added GCB 3D files
    [assembly.scad, cap.scad, cherry_mx_cap.scad, chinese_laser.scad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]
2016-03-26 button test bases
    [button_base.fcstd, button_base_1.blend]
2016-03-26 fixed geometry on button base
    [button_base.fcstd]
2016-03-26 changed button base size
    [button_base.fcstd]
2016-03-27 button base no. 2, has fillets
    [button_base.fcstd]
2016-03-27 updated sliding keyboard laser file
2016-04-03 added sprint recesses in button base
    [button_base.fcstd]
2016-04-03 thicker side wall, mouting recesses for rubber base
    [button_base.fcstd]
2016-04-04 modified button cap to print better
    [cap.scad, cherry_mx_cap.scad, cherry_mx_cap.stl]
2016-04-04 clip hatch for button base
    [button_hatch.fcstd]
2016-04-04 button base deeper wells
    [button_base.fcstd]
2016-04-05 removed 5mm of height from button base
    [button_base.fcstd]
2016-04-05 removed fillets from button for easier revisions later
    [button_base.fcstd]
2016-04-05 carved another 7mm out of button_base
    [button_base.fcstd]
2016-04-05 more aggressive anti-warp patterning
    [button_base.fcstd]
2016-04-07 working on button stabilizer
    [button_base.fcstd, button_hatch.fcstd]
2016-04-07 lowered button 4mm
    [button_base.fcstd]
2016-04-11 refactored openscad code to produce sabilized keycaps
    [cap.scad, cherry_mx_cap.scad, cherry_mx_cap.stl, keycap_mount.scad]
2016-04-13 button revision for tasc meeting
    [button_base.fcstd]
2016-04-13 removed stabilizers from button
    [button_base.fcstd]
2016-04-14 button_base redesigned for lever-cap.
    [button_base.fcstd]
2016-04-14 openscad button cap redesign
    [cap.scad, cherry_mx_cap.scad, cherry_mx_cap.stl, keycap_mount.scad]
2016-04-15 Starting a huge button_base rewrite
    [button_base.fcstd, button_base.scad]
2016-04-17 button rewrite in openscad
    [button_base.scad]
2016-08-05 testing computer control with button to 3.5mm audio input
2016-08-05 Cleaned up models folder
    [assembly.scad, base.fcstd, braille.fcstd, button_base.fcstd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]
2016-08-30 Fixed variable issue and cleaned up formatting for button cap scad.
    [button_base.scad, cap.scad]
2016-08-31 trying different values with the button cap
    [button_base.scad, cap.scad]
